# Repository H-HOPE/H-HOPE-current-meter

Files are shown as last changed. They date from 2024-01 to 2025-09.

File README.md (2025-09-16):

<div align="right">
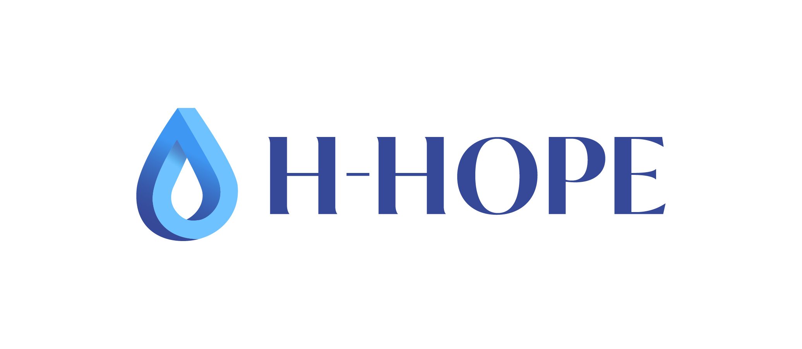
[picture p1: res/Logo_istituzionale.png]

</div>

# DIY water current meter for measuring flow velocities 'H-HOPE water current meter'

The water current meter "H-HOPE water current meter" was designed and developed as part of a H-HOPE project (web site https://h-hope.eu/). H-HOPE water current meter measures water flow velocities on the principle of automatic recalculation of screw rotation frequencies in water velocity through the equation. H-HOPE water current meter has been designed to be produced using the DIY (Do-It-Yourself) principle. All parts used for the production of H-HOPE water current meter are readily available. H-HOPE water current meter can be powered by 9V battery, or by external micro USB cable. H-HOPE water current meter can measure water velocity from 0.1 to 5m/s. 

<div align="center">
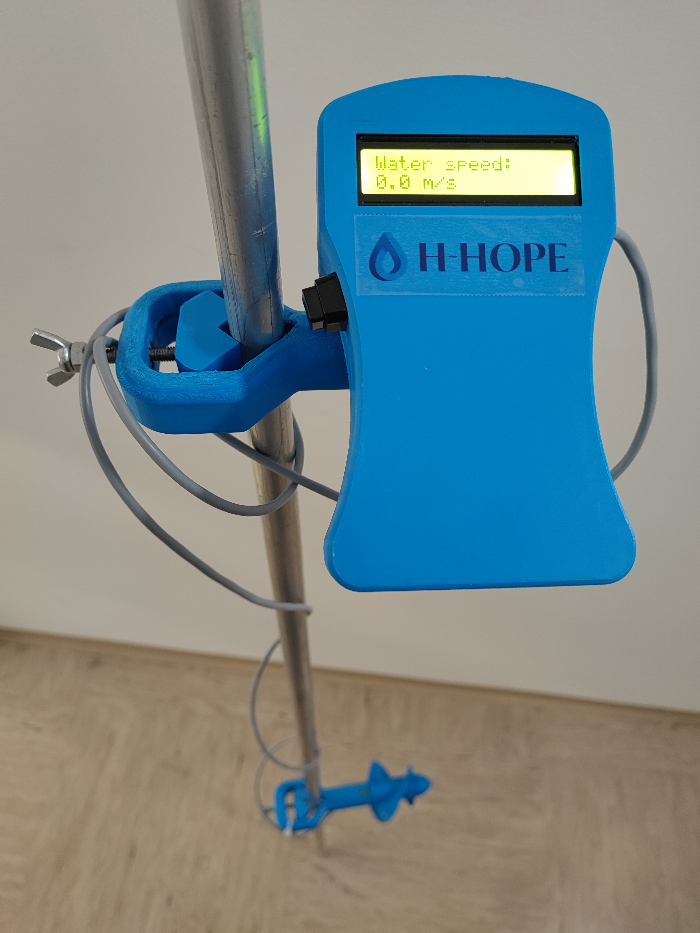
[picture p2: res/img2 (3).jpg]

 
Figure. H-HOPE water current meter.</div>

<div align="center">
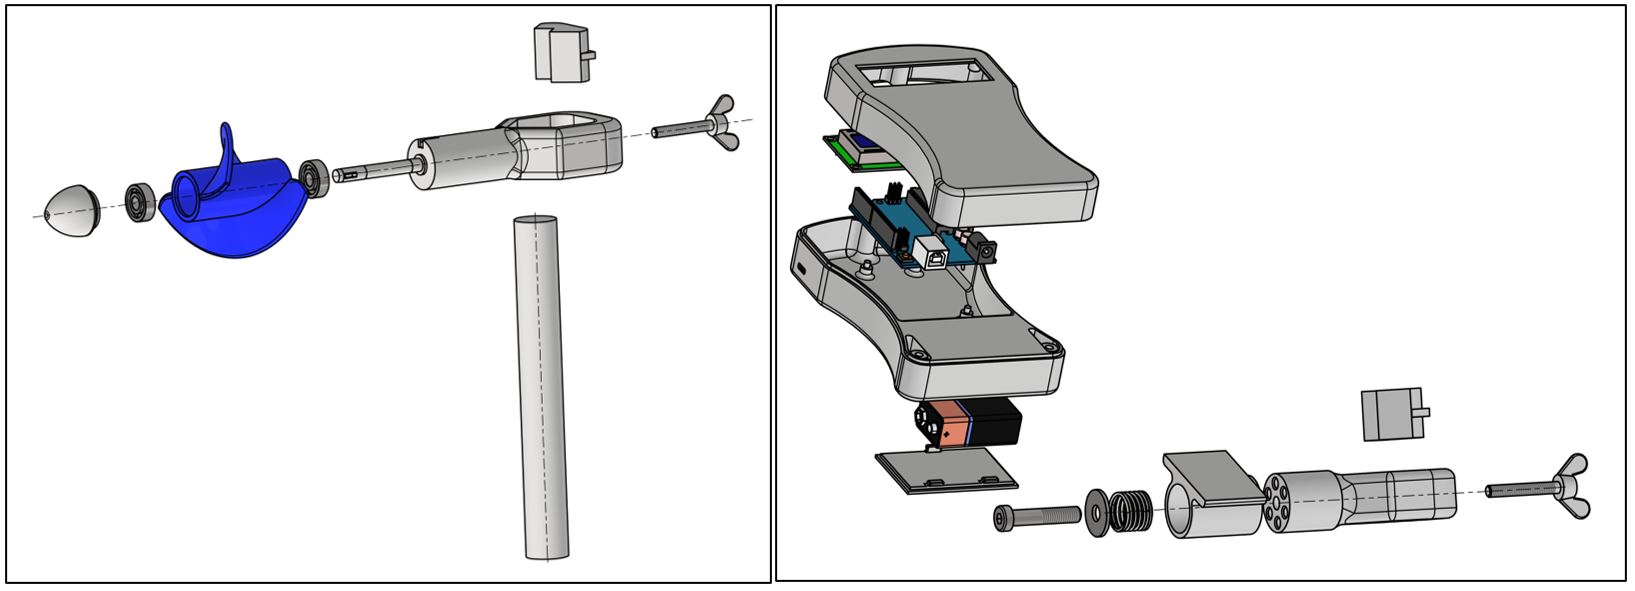
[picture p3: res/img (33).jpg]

 
Figure. 3D exploded model of a H-HOPE water current meter.</div>

## Table of content

- [Materials and tools,](#material)
- [3D model,](#3dmodel)
- [Arduino code,](#arduino)
- [Assembly and test,](#assembly)
- [Field test.](#fieldtest)

## Material and tools used

The project was designed in a certain way, that the material and tools necessary to build this project is widely available. Most of the parts and tools are available in local technical store or for example on online store Aliexpress. 

### Material used for this project:

- Arduino uno https://www.aliexpress.com/item/1005002707450245.html
- Connectors (XH): https://www.aliexpress.com/item/33000442968.html
- Connecting cables (XH): https://www.aliexpress.com/item/1005002160765607.html
- Micro usb socket: https://www.aliexpress.com/item/1005003730290423.html
- 9v battery holder https://www.aliexpress.com/item/32825539506.html
- 16x2 LCD with i2c header: https://www.aliexpress.com/item/32413056677.html
- Unipolar Hall sensor (SIP package, for exmaple SS443A): https://www.aliexpress.com/item/1005001522952951.html
- Magnet, size 3x1mm: https://www.aliexpress.com/item/1005005222147418.html
- 2m 3-core cable: https://www.aliexpress.com/item/1005002082473369.html
- Pushbutton / toggle ON/OFF switch: https://www.aliexpress.com/item/1005004004236347.html
- XH pin connectors: https://www.aliexpress.com/item/1005004267331222.html
- 6x M2 screws (10mm length)
- 3x M4 screws (30mm length)
- 2x M5 screws with 
- M8 screw (50mm length)
- Epoxy glue
- 9v battery
- micro usb cable
- spring
- Stick, Bar

### Tools needed for this project:

- Soldering iron
- 3D printer
- Set of Screwdrivers

## 3D printing and model of the H-HOPE water current meter

We used Prusa MK3S 3D printer to print the H-HOPE water current meter plastic parts. Chosen material was PETG.

Below is the 3D exploded model of a H-HOPE water current meter. H-HOPE water current meter is made from two main parts. 

- assembly of a screw,
- assembly of the enclosure with LCD screen and holder. 

<div align="center">
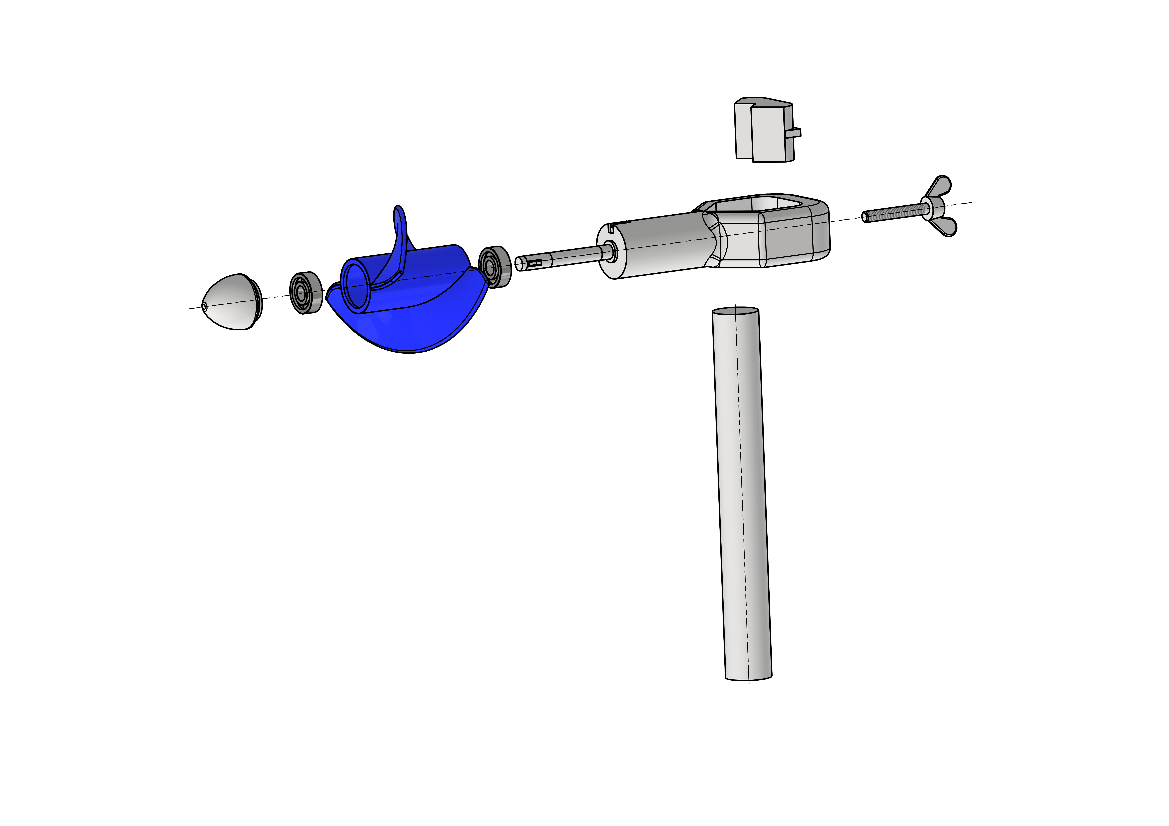
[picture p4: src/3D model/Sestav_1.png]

 
Figure. Exploded model of the screw.</div>

<div align="center">
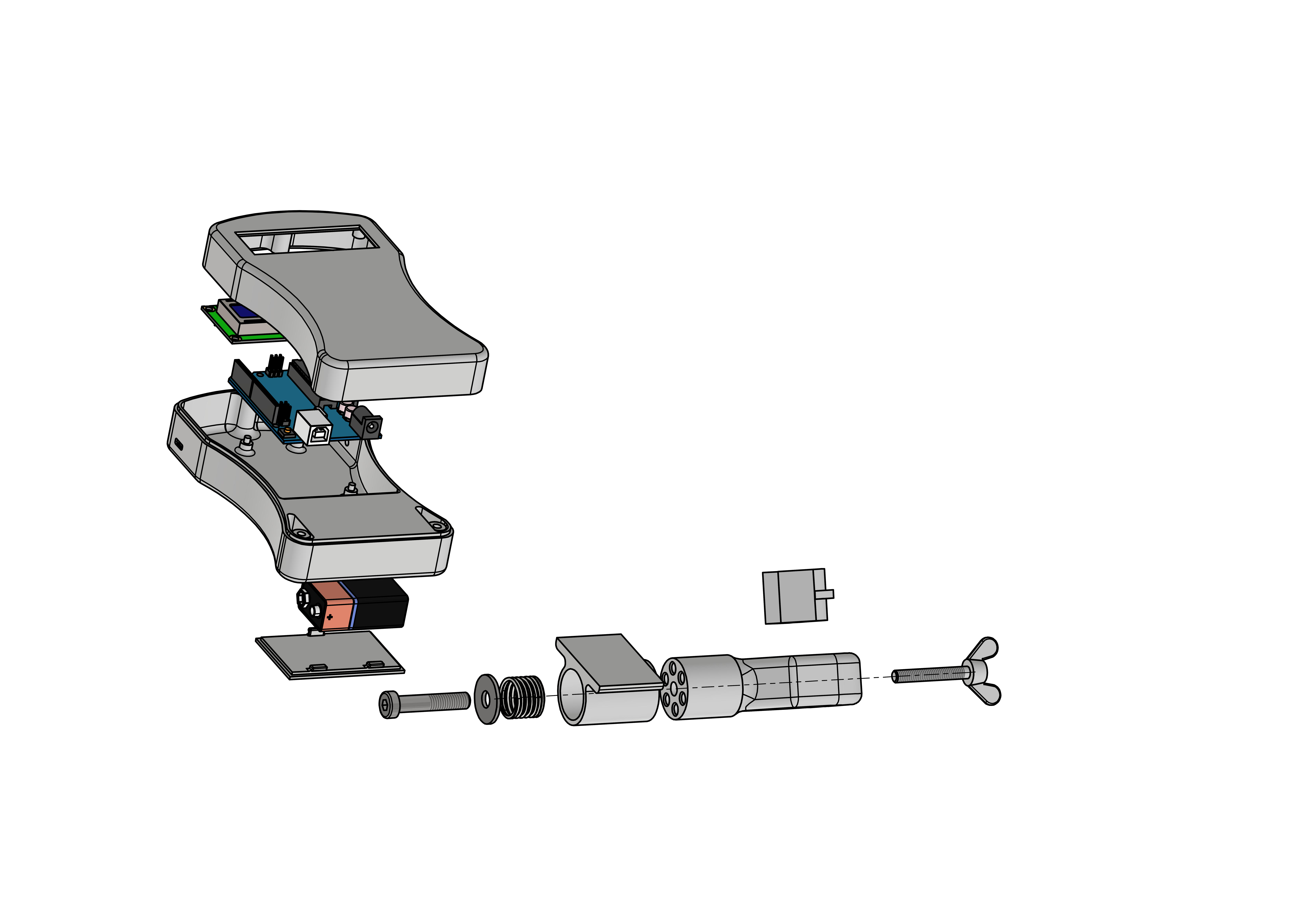
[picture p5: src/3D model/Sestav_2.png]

 
Figure. Exploded model of the enclosure with LCD screen and holder.</div>

Source files (in STEP and STL format) for printing the H-HOPE water current meter are available on Github: [STEP files](https://github.com/H-HOPE/H-HOPE-current-meter/tree/main/src/3D%20model/STEPfiles), [STL files](https://github.com/H-HOPE/H-HOPE-current-meter/tree/main/src/3D%20model/STLfiles).

<div align="center">
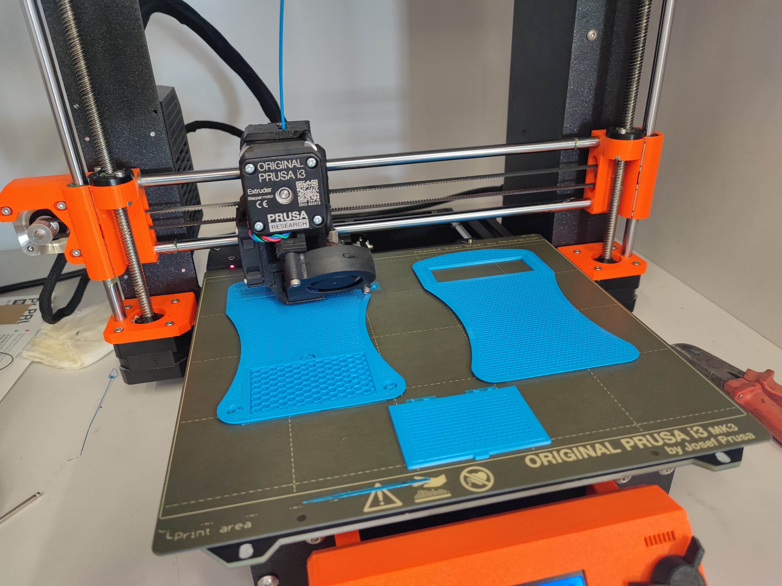
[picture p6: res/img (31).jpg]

 
Figure. Printing the H-HOPE water current meter enclosure.</div>

<div align="center">
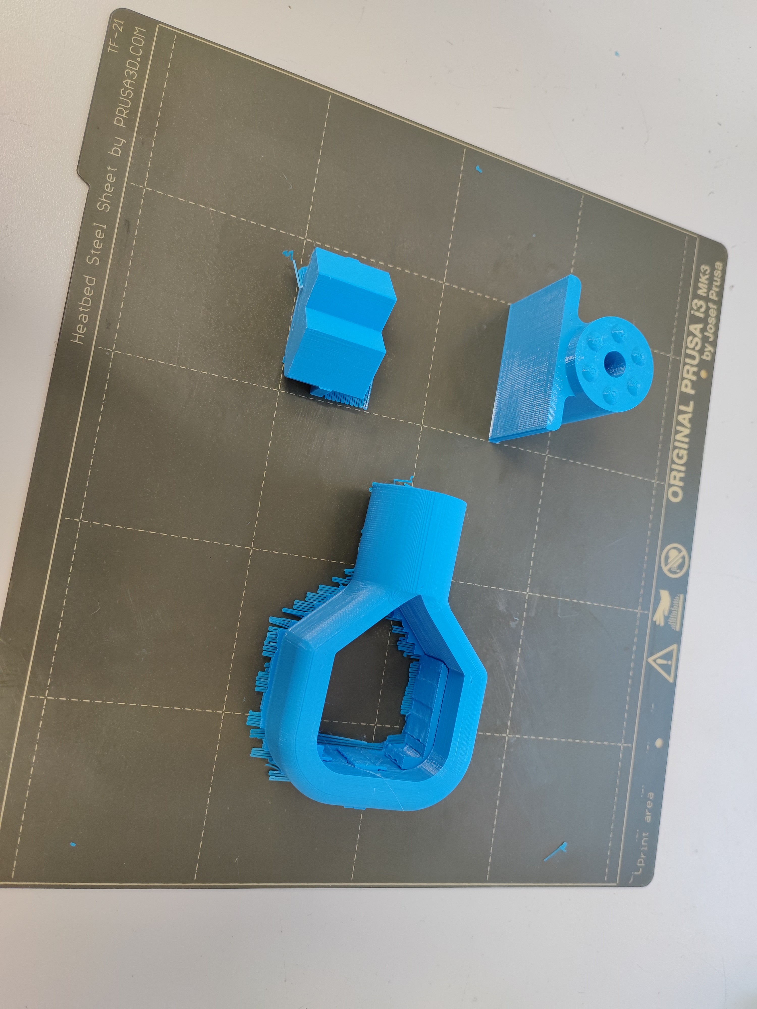
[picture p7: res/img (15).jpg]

 
Figure. 3D printed parts for the H-HOPE water current meter holder.</div>

## Arduino code

In this chapter the source code for the Arduino Uno microcontroller will be explained.

<div align="center">
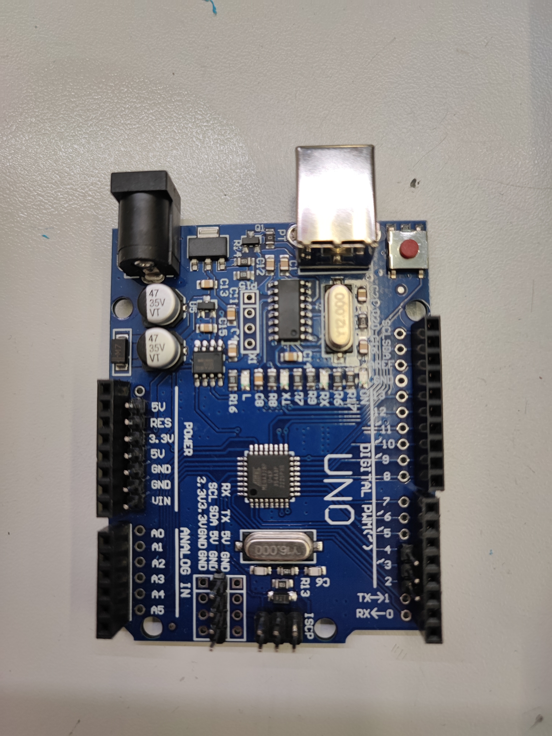
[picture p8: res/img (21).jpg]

 
Figure. Arduino uno board is used for H-HOPE water current meter electronics.</div>

Arduino code:
https://github.com/H-HOPE/DIY_Flow_meter/blob/e5a896e44799b07652782b1dd13d3e7614e1950c/src/Arduino/H-HOPE_Hi-wing.ino#L1-L63

Key parts of the Arduino code:
- First, we include libraries for LCD screen and I2C protocol. LCD screen library is also available [here](https://github.com/H-HOPE/DIY-Flow-meter/tree/main/src/Arduino/lib).
- Then we define an Arduino pin, where the hall sensor will be connected. In this case, this pin is number 2.
- in lines 13 through 15 we define variables. 
- In the setup section we initialize the LCD screen and configure interrupt for the hall sensor. 
Hall sensor output is connected to the Arduino Uno inetrrupt. Arduino Uno has two external interrupt pins, INT0 and INT1, which are mapped to digital pins 2 and 3 respectively. Interrupts are signals that allow a microcontroller to pause its current execution and handle an event or task that has a higher priority. 
In this case hall sensor is attached to the INT0 pin (digital pin 2).
Configure the interrupt settings using the attachInterrupt() function. This function takes three arguments: the interrupt number (in this case, 0 for INT0), the function to call when the interrupt is triggered (cnt), and the mode in which to trigger the interrupt (on FALLING EDGE).
- In the loop section, from line 38, the code to calculate the water velocity from the screw rotation speed is written. The calculated water velocity is shown on the LCD screen.
- Finally at the end of the program there is an interrupt routine, that records the time when the magnet on the wing passes hall sensor.

<div align="center">
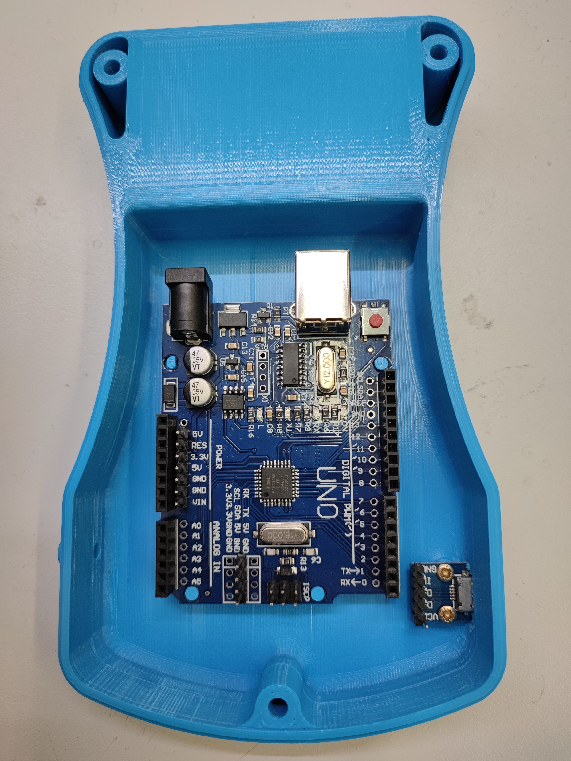
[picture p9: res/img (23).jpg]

 
Figure. Arduino Uno microcontroller mounted in the H-HOPE water current meter enclosure.</div>

## Assembly and test

With all the printed parts ready and programmed Arduino, we can start the assembly of the H-HOPE water current meter.

3D exploded model of a H-HOPE water current meter

<div align="center">

 
Figure. 3D exploded model of a screw.</div>

<div align="center">

 
Figure. 3D exploded model of the enclosure.</div>

### Enclosure for the H-HOPE water current meter electronics

<div align="center">
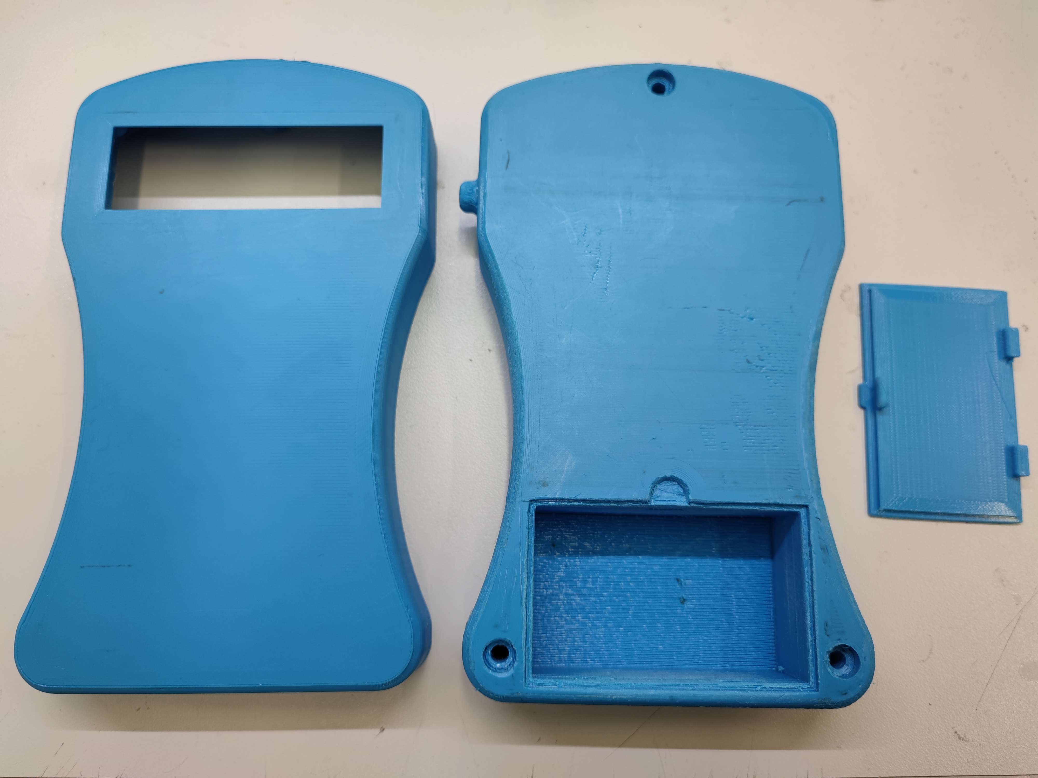
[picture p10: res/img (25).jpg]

 
Figure. Enclosure for the H-HOPE water current meter electronics.</div>

Assembly of the screw:

Mount two bearings in the screw and put the end cap to the screw.

<div align="center">
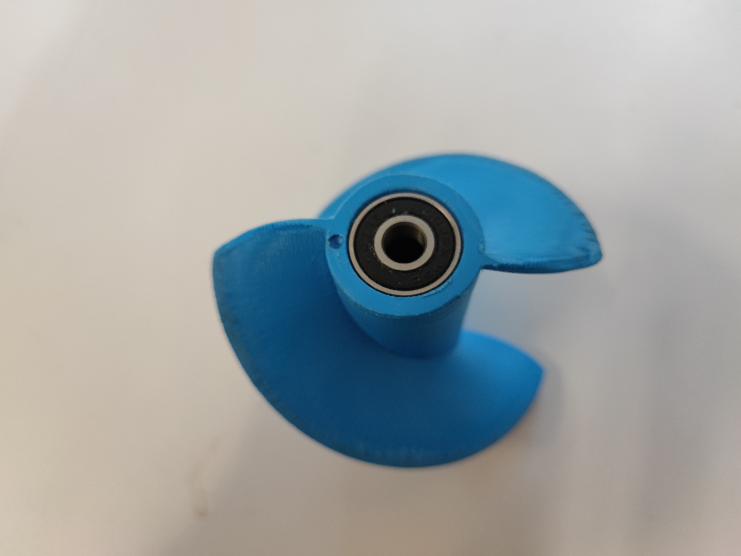
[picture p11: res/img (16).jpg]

 
Figure. First bearing mount.</div>

<div align="center">
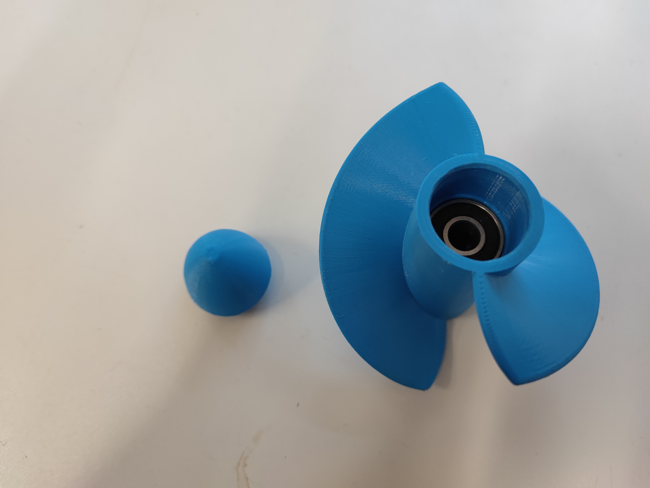
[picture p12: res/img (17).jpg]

 
Figure. Second bearing mount, with end cap.</div>

<div align="center">
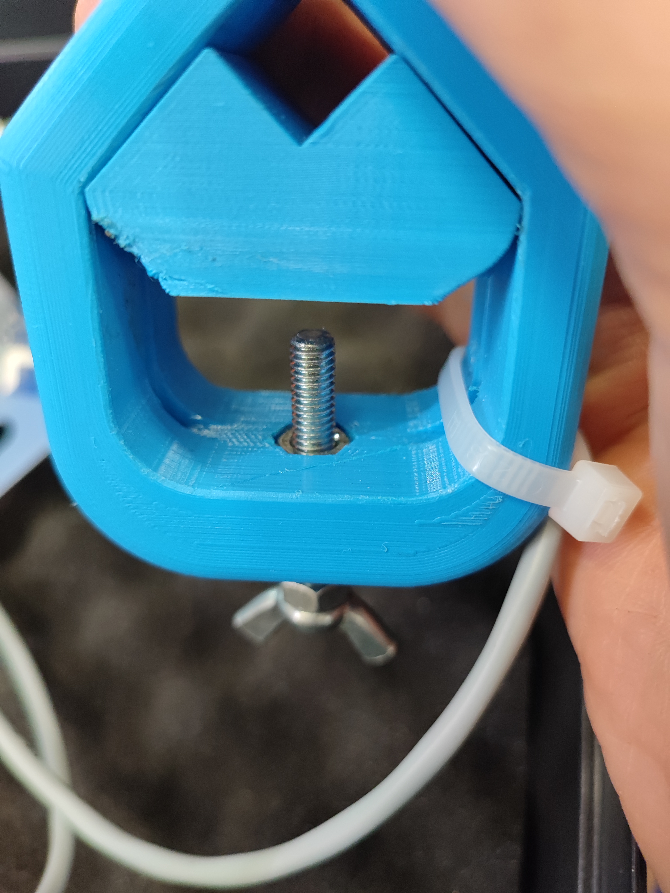
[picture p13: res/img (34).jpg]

 
Figure. Assembly of the bar mounting tight screw</div>

<div align="center">
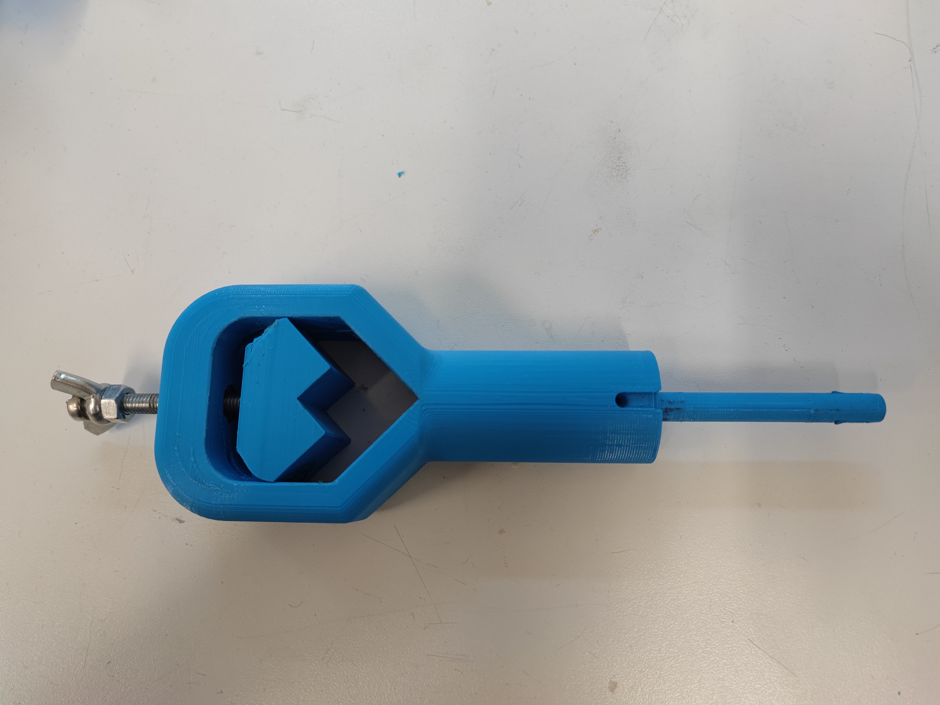
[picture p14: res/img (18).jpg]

 
Figure. Assembled screw holder.</div>

Next, place 1x3 mm magnet in the prefabricated hole in the screw and glue the magnet with Epoxy glue.
<div align="center">
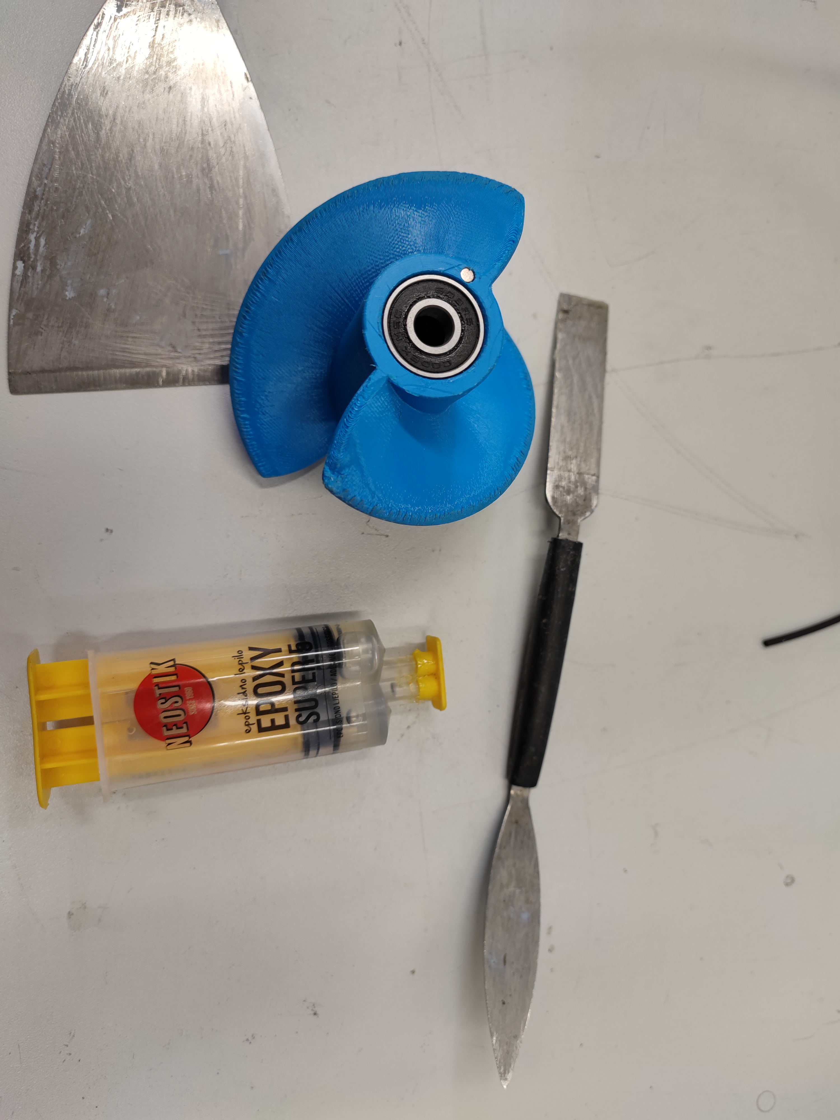
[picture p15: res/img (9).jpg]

 
Figure. Magnet assembly on the screw.</div>

We need to solder hall sensor to the cable. Hall sensor has three pins GND, VCC and Signal

<div align="center">
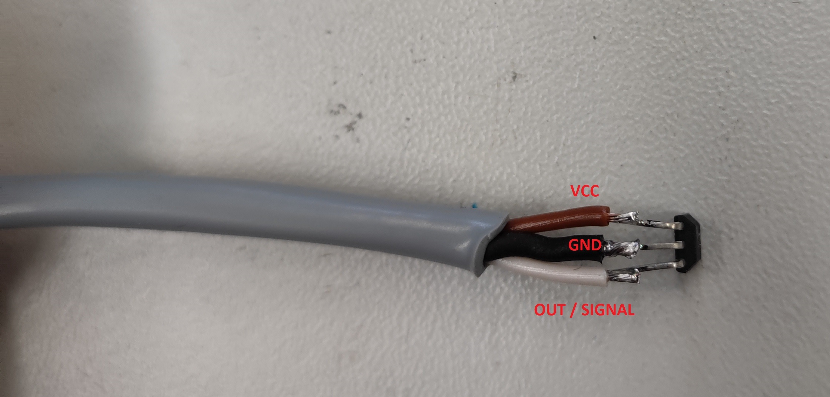
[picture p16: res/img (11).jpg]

 
Figure. Pinout of the SS443a Hall sensor.</div>

Put the cable through the screw holder and glue the hall sensor, with the Epoxy glue to the screw holder.

<div align="center">
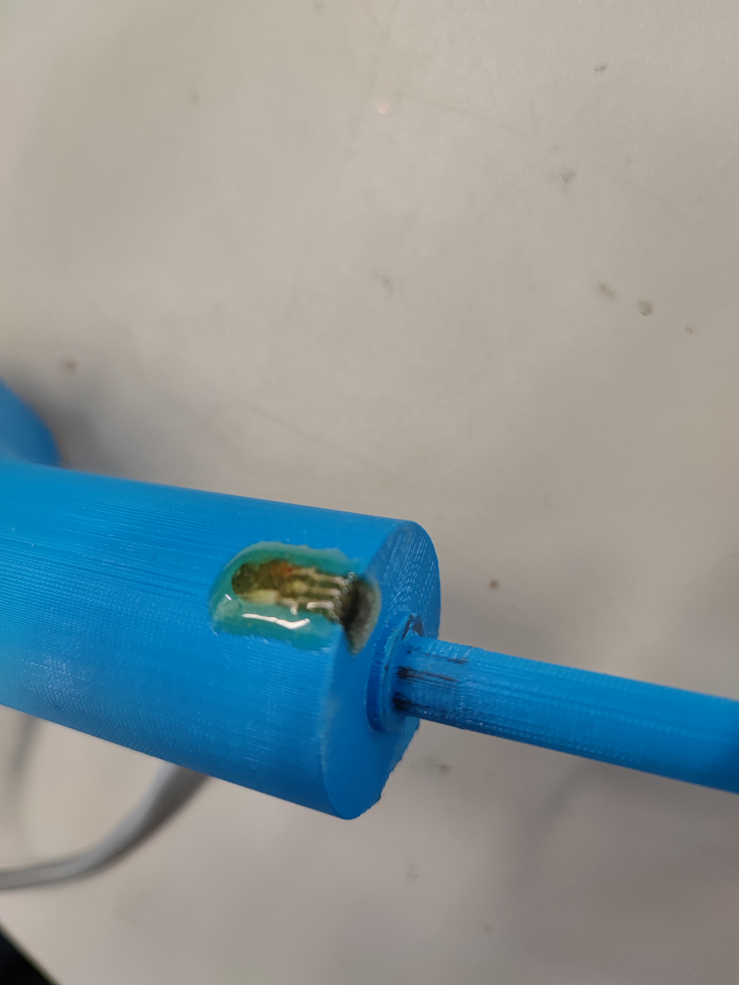
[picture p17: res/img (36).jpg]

 
Figure. Screw with bearing and end cap.</div>

Assembled Screw.
<div align="center">
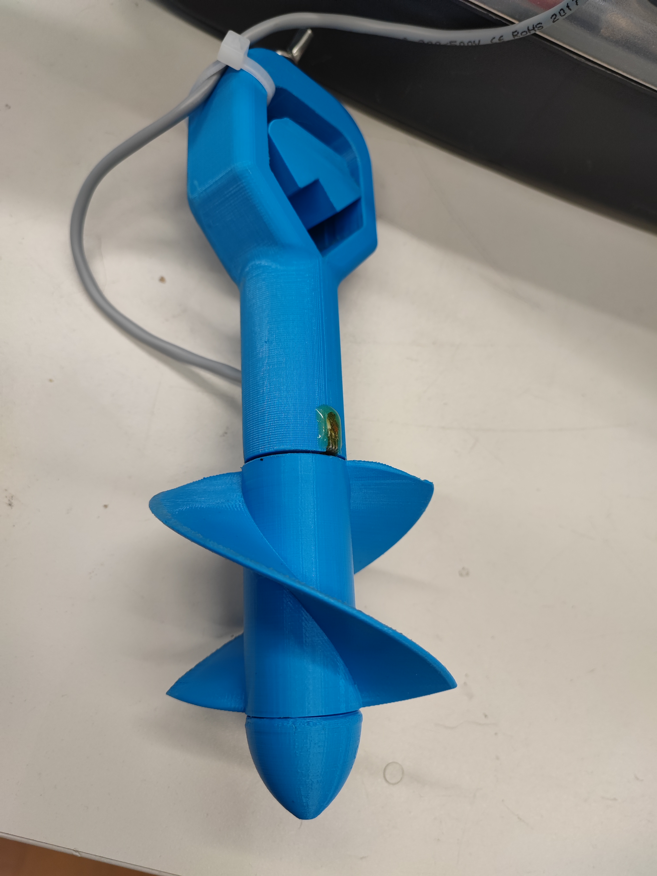
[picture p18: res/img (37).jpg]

 
Figure. Assembled Screw.</div>

### Assembly of the H-HOPE water current meter electronics.

Mount the Arduino Uno in the enclosure, screw the micro USB module to the enclosure with two M2 10mm screws. Connect micro USB module to Arduino Uno (5V to 5V; GND to GND).
<div align="center">

 
Figure. Arduino Uno and micro USB module.</div>

Connect hall sensor GND, VCC and OUT to the Arduino Uno
<div align="center">
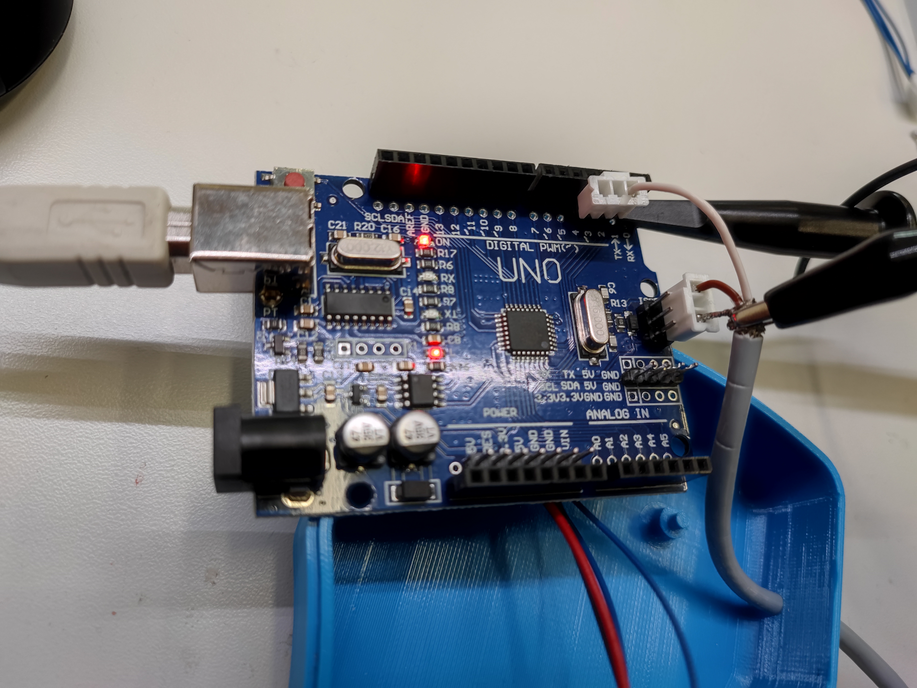
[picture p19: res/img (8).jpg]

 
Figure. Hall sensor connected to the Arduino Uno.</div>

Mount 16x2 LCD screen with 4 M2 10mm screws to the front of the enclosure. Connect the LCD screen to the Arduino, through the I2C protocol.
<div align="center">
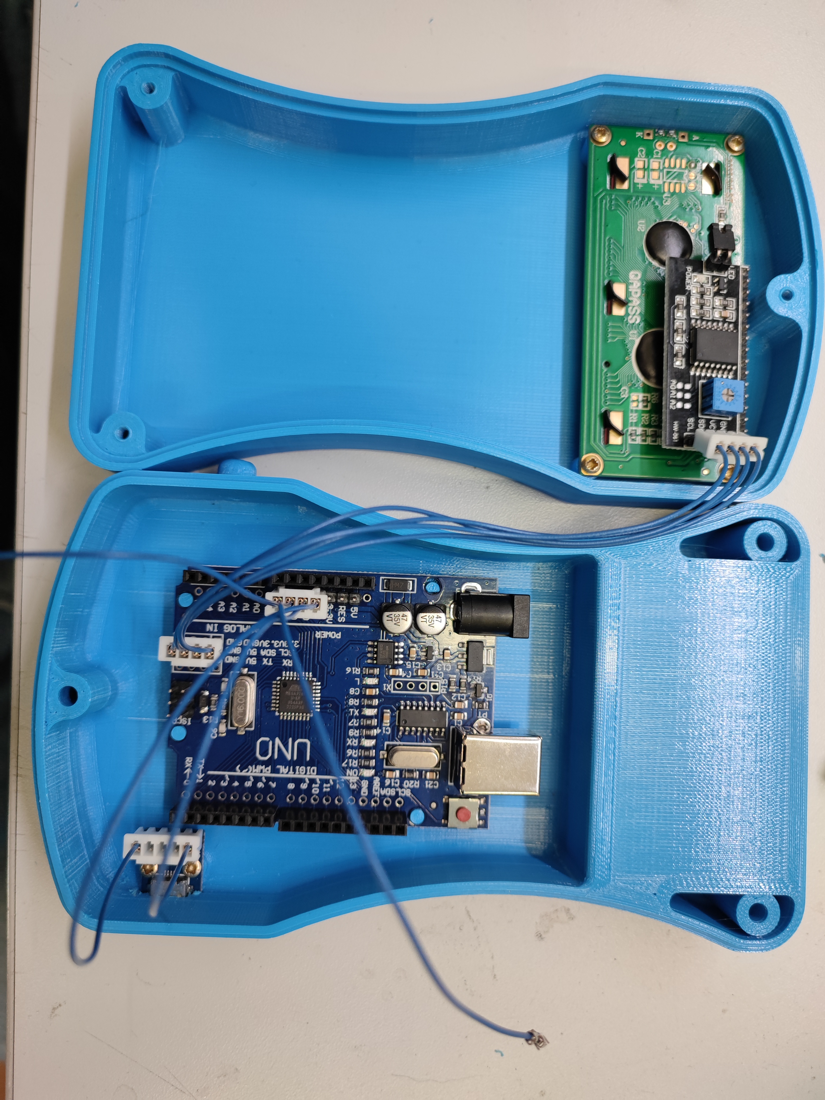
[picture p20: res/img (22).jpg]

 
Figure. LCD screen connection.</div>

Mount 9V battery connector, make small hole for wires. Connect 9v Battery holder to Arduino Uno (+9V battery to Vin Arduino Uno pin; -9V battery to GND Arduino Uno pin)
<div align="center">
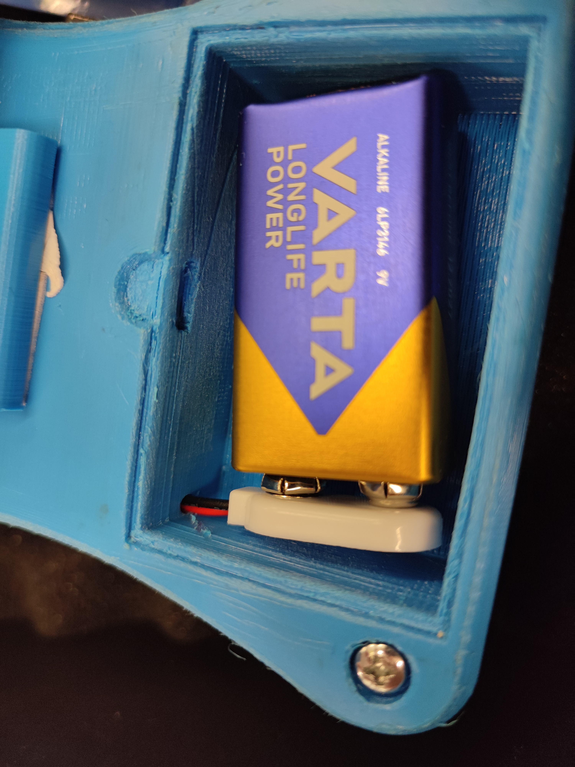
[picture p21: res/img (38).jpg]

 
Figure. 9V battery installation.</div>

Make hole on the enclosure for the external ON/OFF switch to power on the H-HOPE water current meter. Connect the switch in series with positive battery wire.
<div align="center">
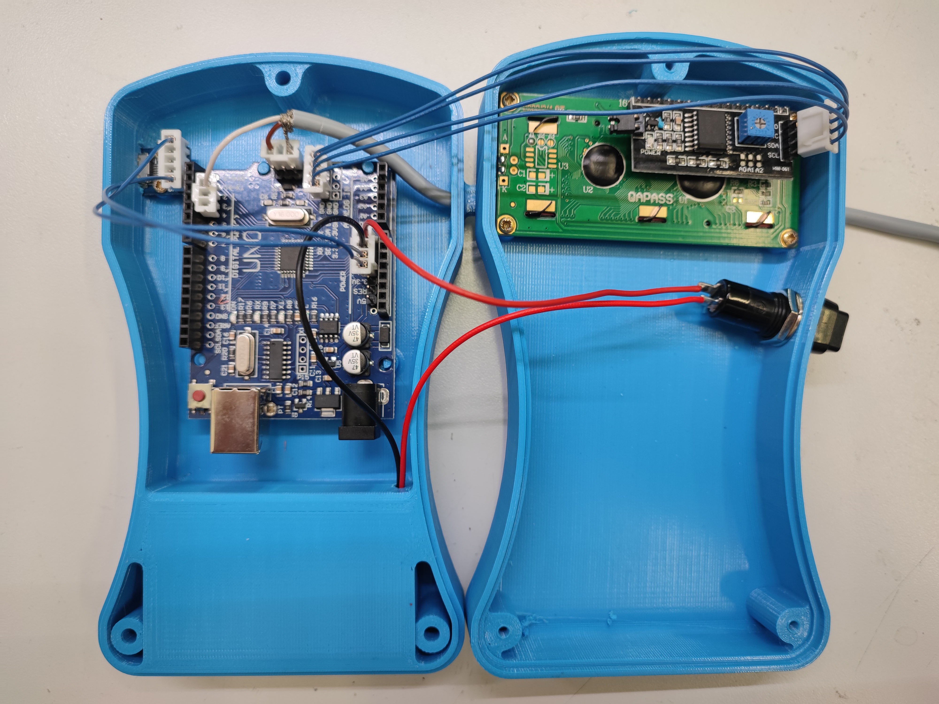
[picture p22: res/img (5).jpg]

 
Figure. External ON/OFF switch.</div>

Use screws to assemble the electronics enclosure of the H-HOPE water current meter. 
<div align="center">
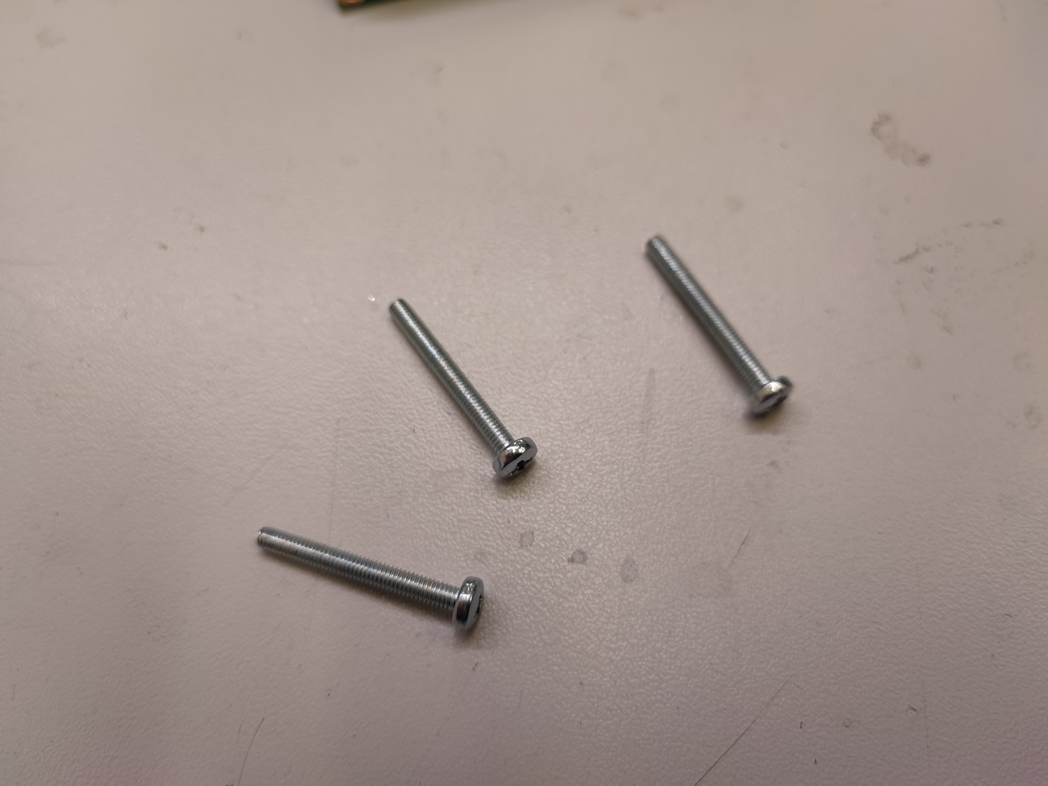
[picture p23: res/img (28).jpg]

 
Figure. Mounting screws.</div>

### Holder for the H-HOPE water current meter electronics (optional)

It is also possible to mount the H-HOPE water current meter electronics with the help of holder to the stick. In that case you need to print and assemble the H-HOPE water current meter holder. 

<div align="center">
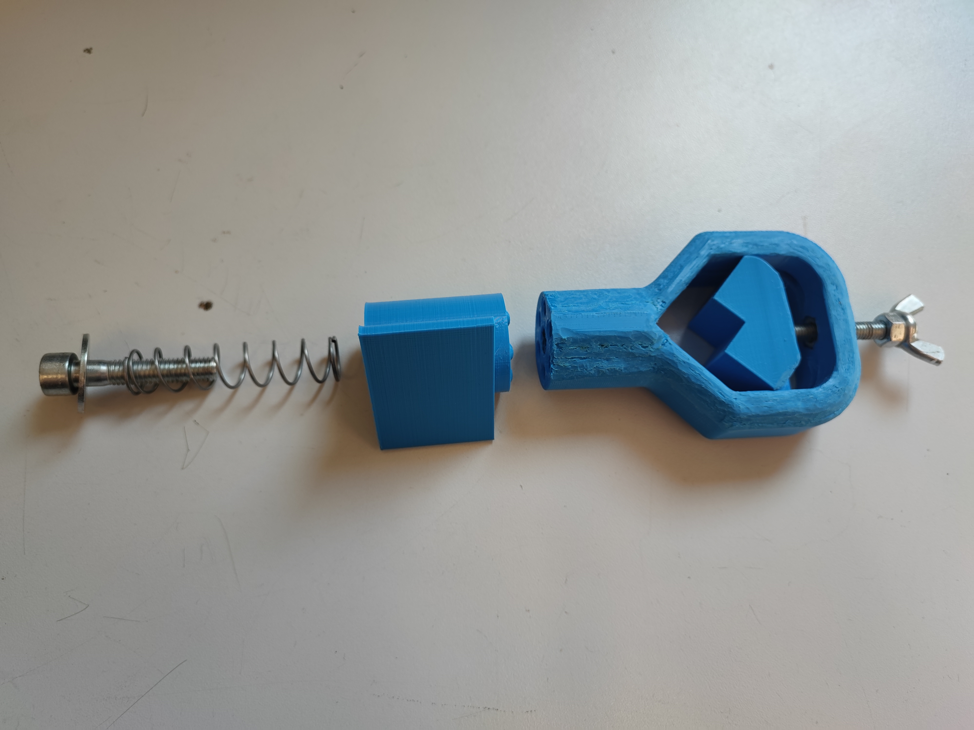
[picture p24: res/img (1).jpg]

 
Figure. Assembly of the holder for the H-HOPE water current meter electronics.</div>

### Test hall sensor response.

Oscilloscope was used to test the output signal from the hall sensor

<div align="center">
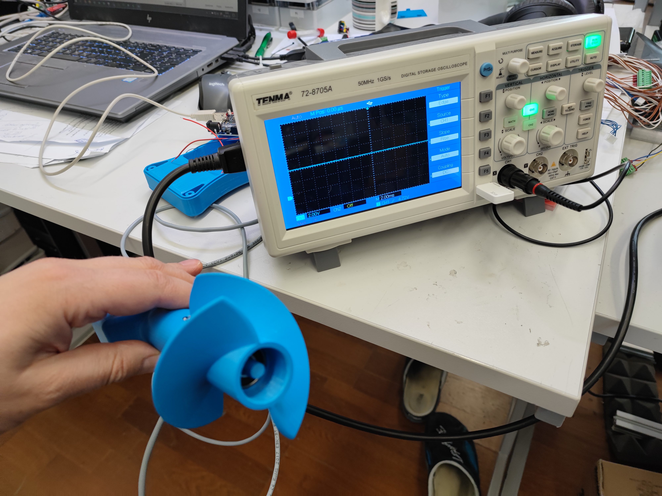
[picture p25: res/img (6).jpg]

 
Figure. Hall sensor test setup.</div>

Hall sensor need pull-up resistor to operate properly. You can use external 10k pull-up resistor across the Vcc and hall input pin. In our case we configured Arduino to use his internal pull-up resistor. Then we test the operation of the hall sensor with an oscilloscope.

<div align="center">
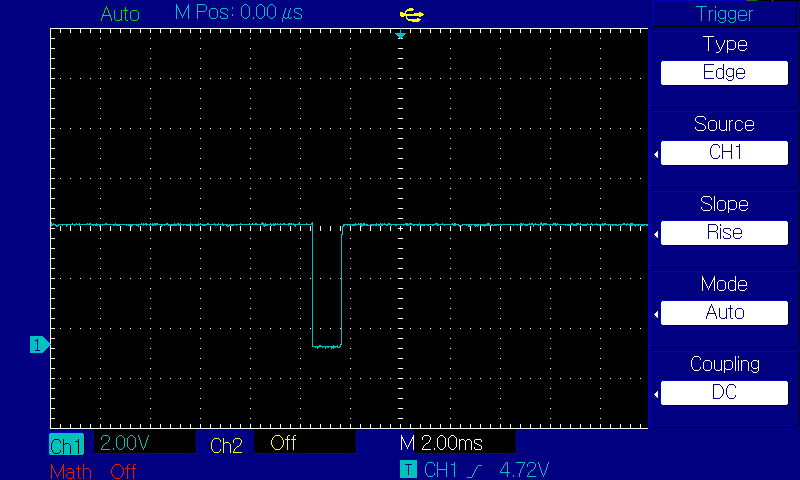
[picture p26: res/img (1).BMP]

 
Figure. Hall sensor output signal on oscilloscope.</div>

## Field test

Now you can find a waterway and measure its speed with the H-HOPE water current meter, water velocity sensor.

<div align="center">
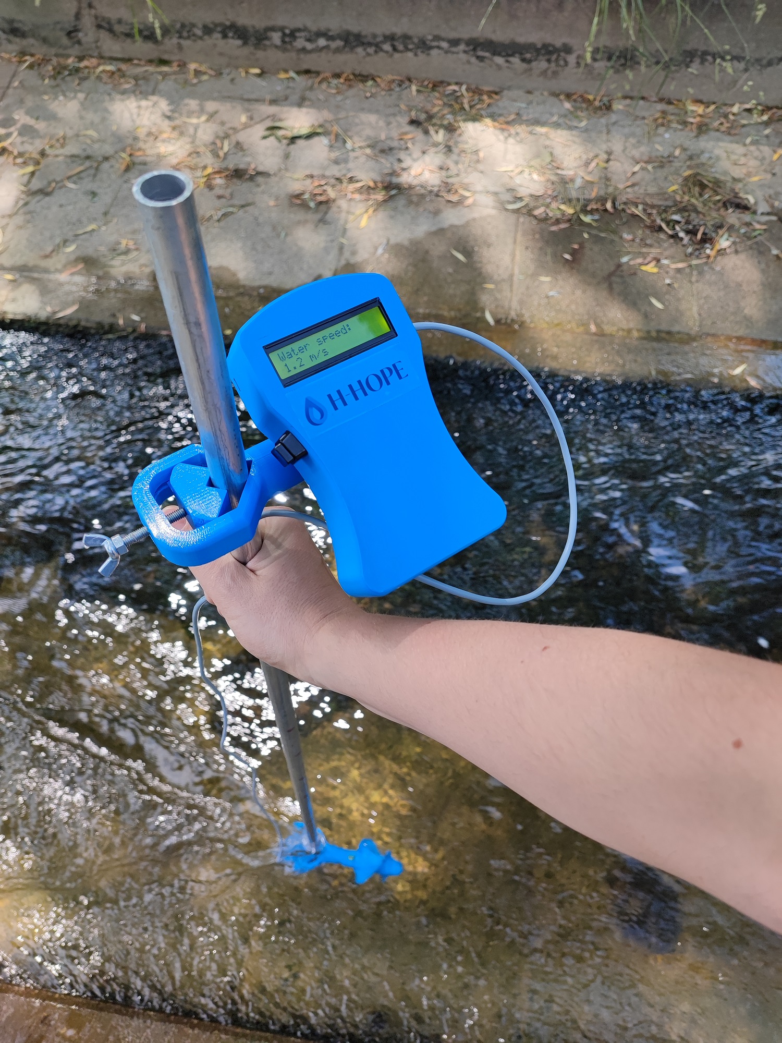
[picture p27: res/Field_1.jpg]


Figure. Image of the H-HOPE water current meter water velocity sensor in open channel
 
 <div align="center">
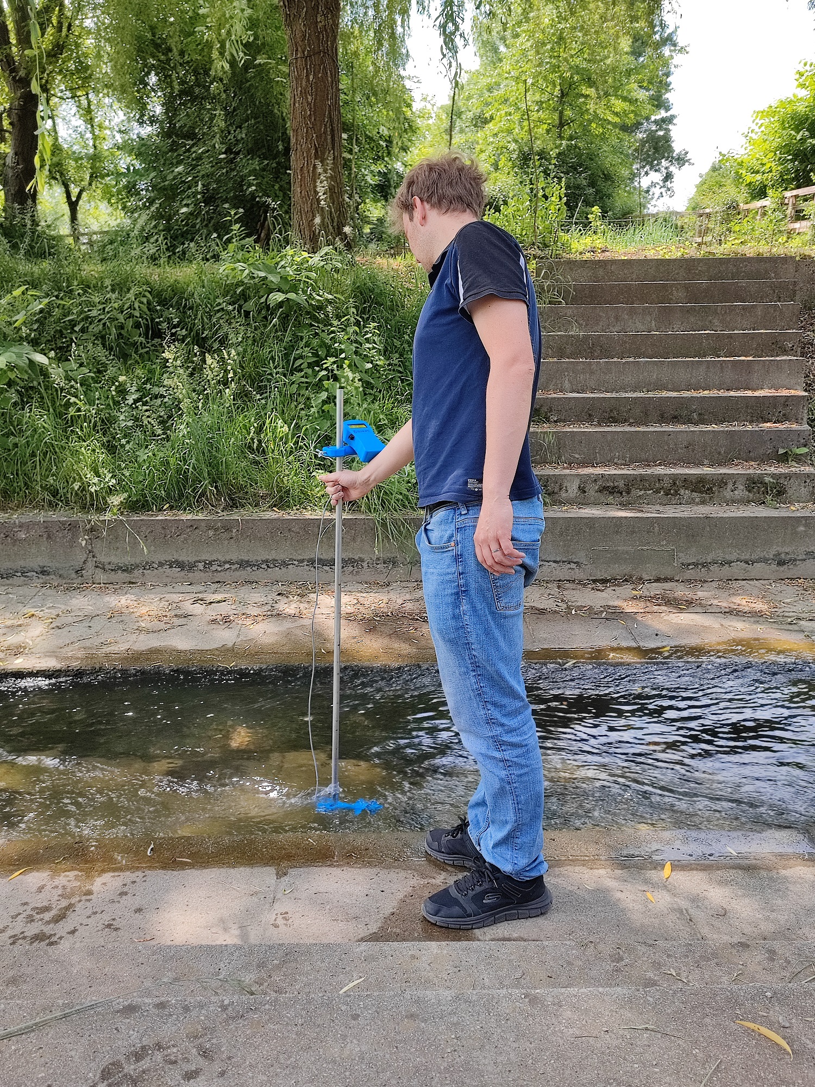
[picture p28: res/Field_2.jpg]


Figure. Measuring water velocity with the H-HOPE water current meter sensor.

&nbsp;
&nbsp;
&nbsp;

<div align="center">
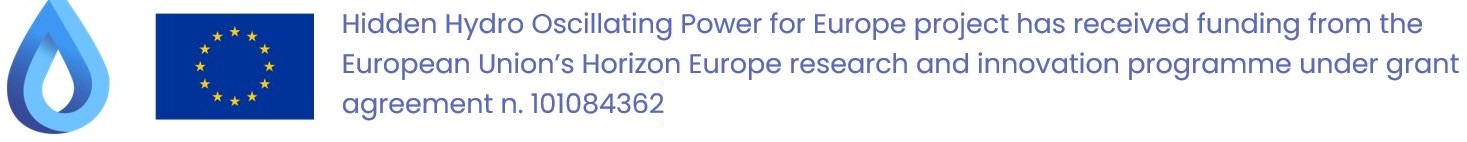
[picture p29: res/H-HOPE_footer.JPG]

</div>

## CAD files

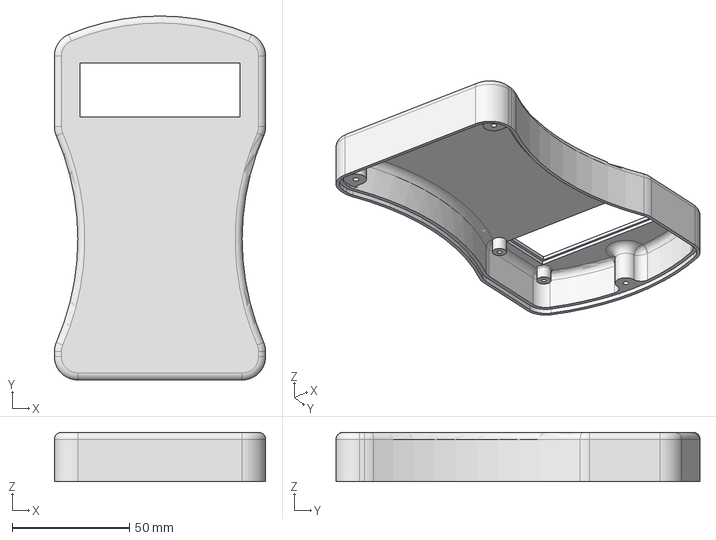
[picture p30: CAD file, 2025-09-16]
src/3D model/STEPfiles/Box Cover.stp
90.0 x 155.0 x 21.0 mm

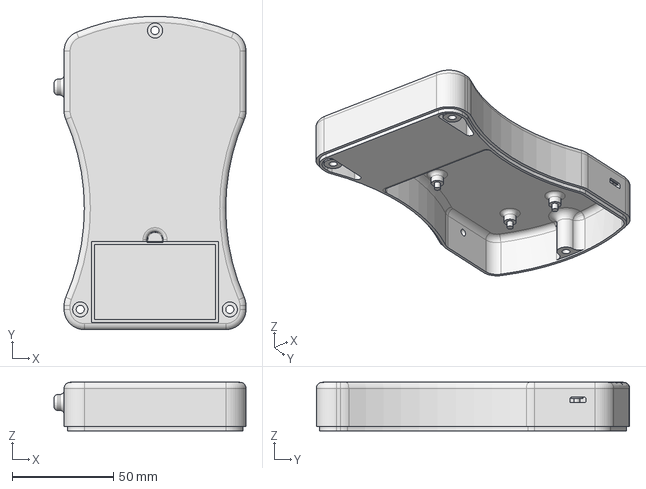
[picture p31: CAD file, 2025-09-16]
src/3D model/STEPfiles/Box Bottom.stp
95.0 x 155.0 x 24.0 mm

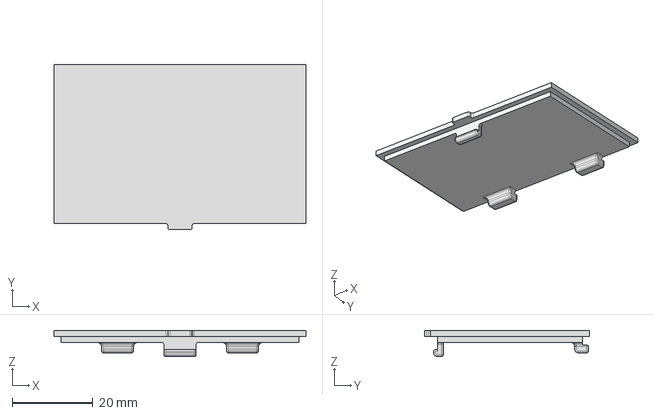
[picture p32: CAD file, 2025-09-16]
src/3D model/STEPfiles/Battery Cover.stp
62.5 x 41.0 x 6.50 mm

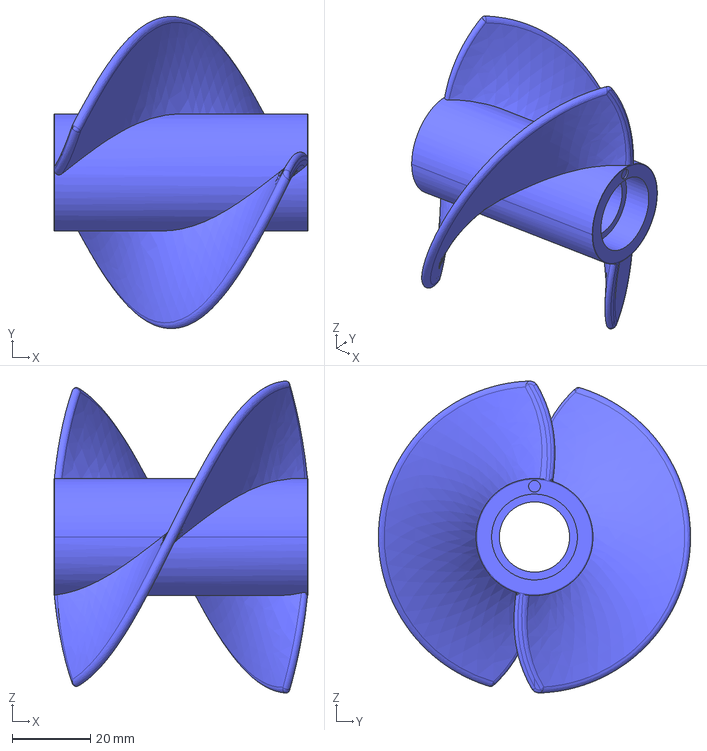
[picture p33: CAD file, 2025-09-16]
src/3D model/STEPfiles/Rotor.stp
65.0 x 80.0 x 80.0 mm

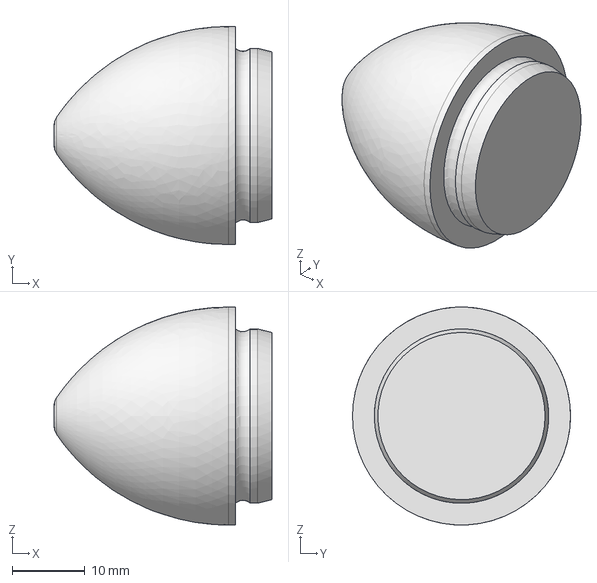
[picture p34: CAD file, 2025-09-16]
src/3D model/STEPfiles/Cap.stp
30.0 x 30.0 x 30.0 mm

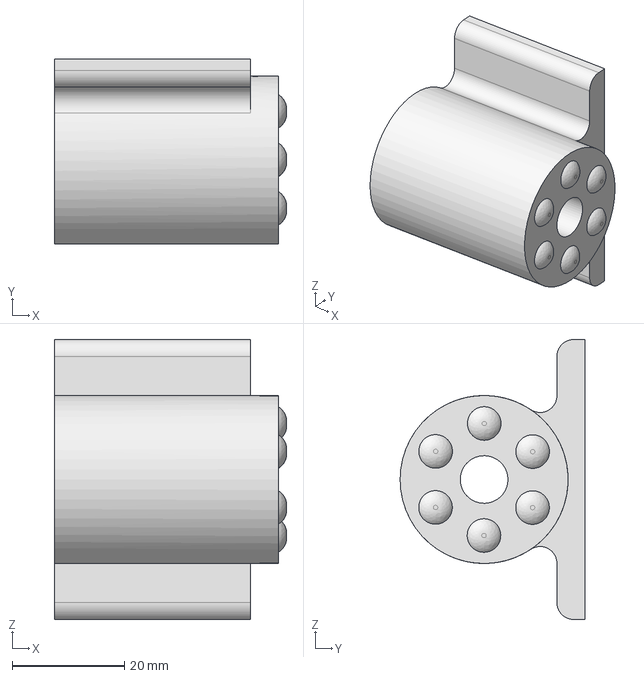
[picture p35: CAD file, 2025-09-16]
src/3D model/STEPfiles/Movable Part of Holder.stp
41.5 x 33.0 x 50.0 mm

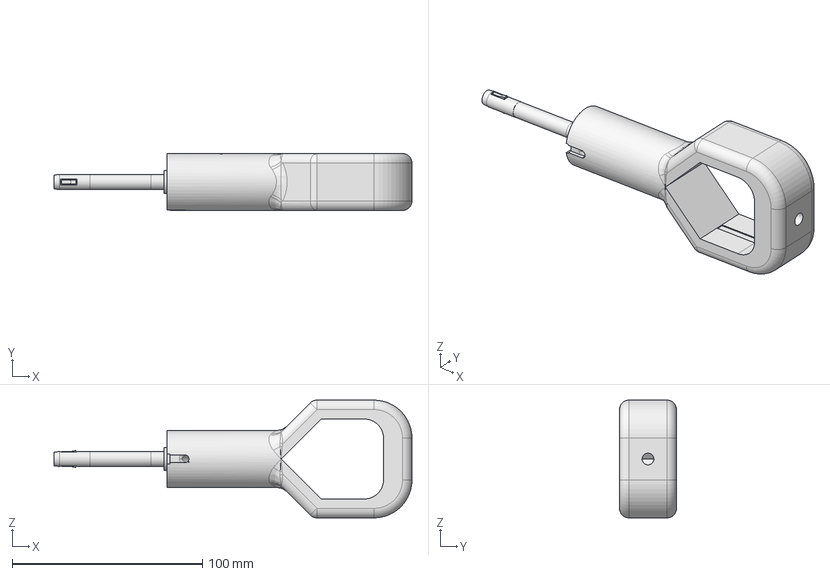
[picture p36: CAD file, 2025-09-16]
src/3D model/STEPfiles/Holder.stp
188.4 x 30.0 x 62.0 mm

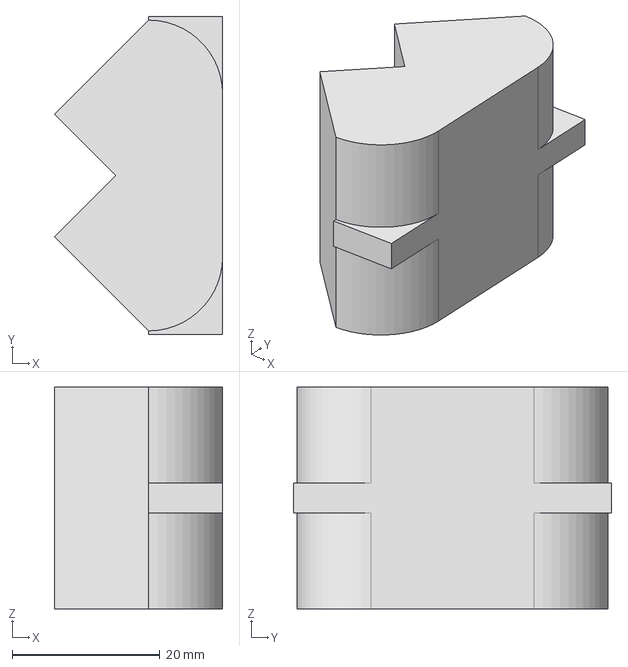
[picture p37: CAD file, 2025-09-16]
src/3D model/STEPfiles/Slider.stp
22.7 x 43.0 x 30.0 mm

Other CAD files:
src/3D model/STLfiles/Battery Cover.stl
src/3D model/STLfiles/Box Bottom.stl
src/3D model/STLfiles/Box Cover.stl
src/3D model/STLfiles/Cap.stl
src/3D model/STLfiles/Holder.stl
src/3D model/STLfiles/Movable Part of Holder.stl
src/3D model/STLfiles/Rotor.stl
src/3D model/STLfiles/Slider.stl
src/3D model/hi_wing_Inventor.iam

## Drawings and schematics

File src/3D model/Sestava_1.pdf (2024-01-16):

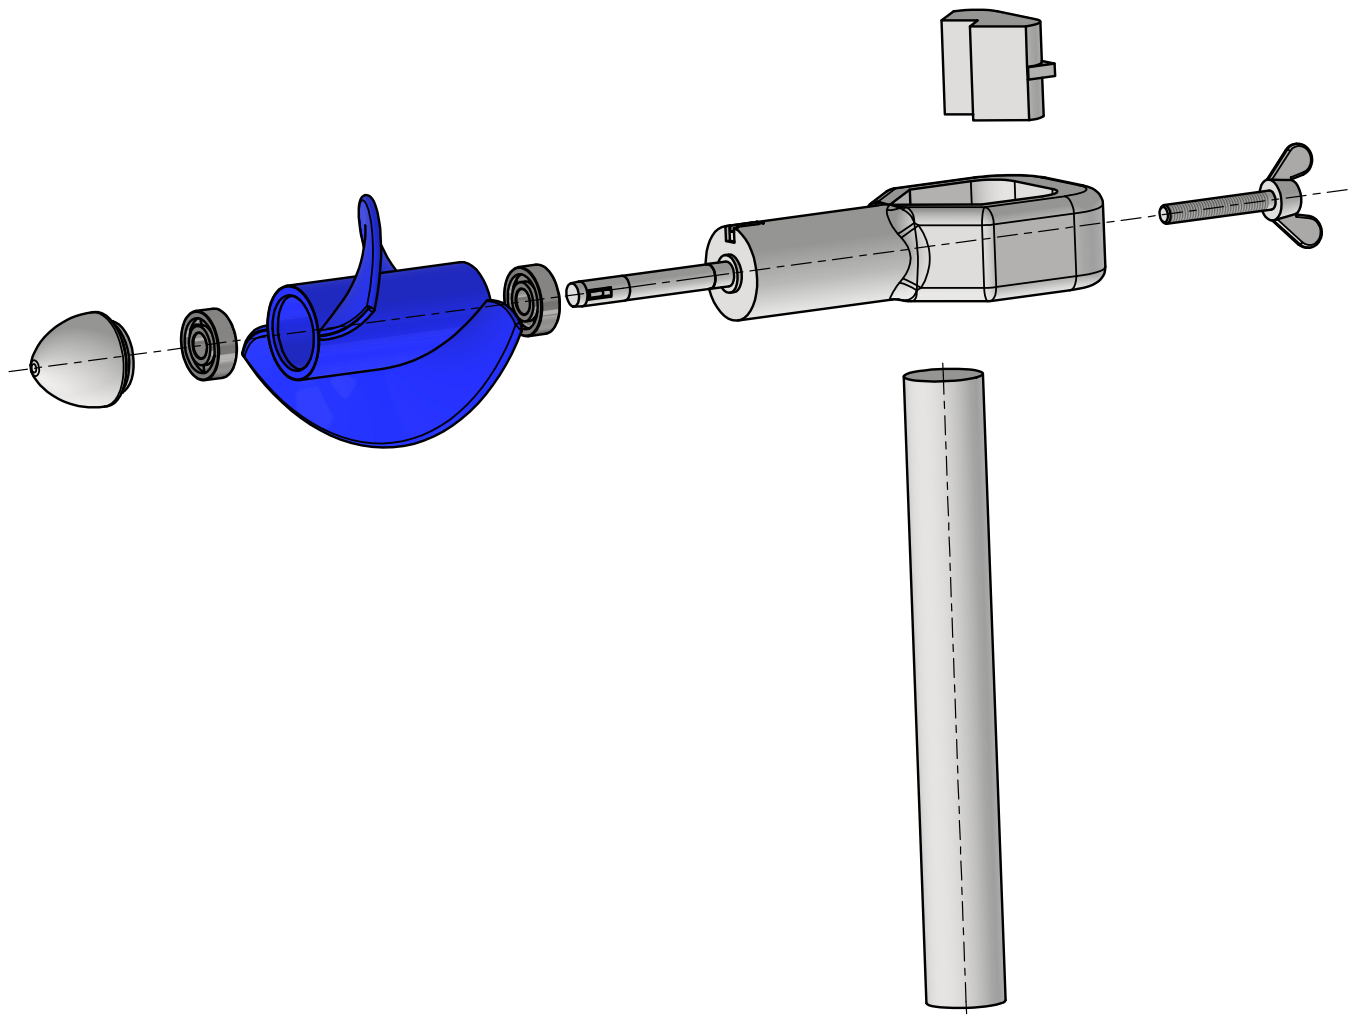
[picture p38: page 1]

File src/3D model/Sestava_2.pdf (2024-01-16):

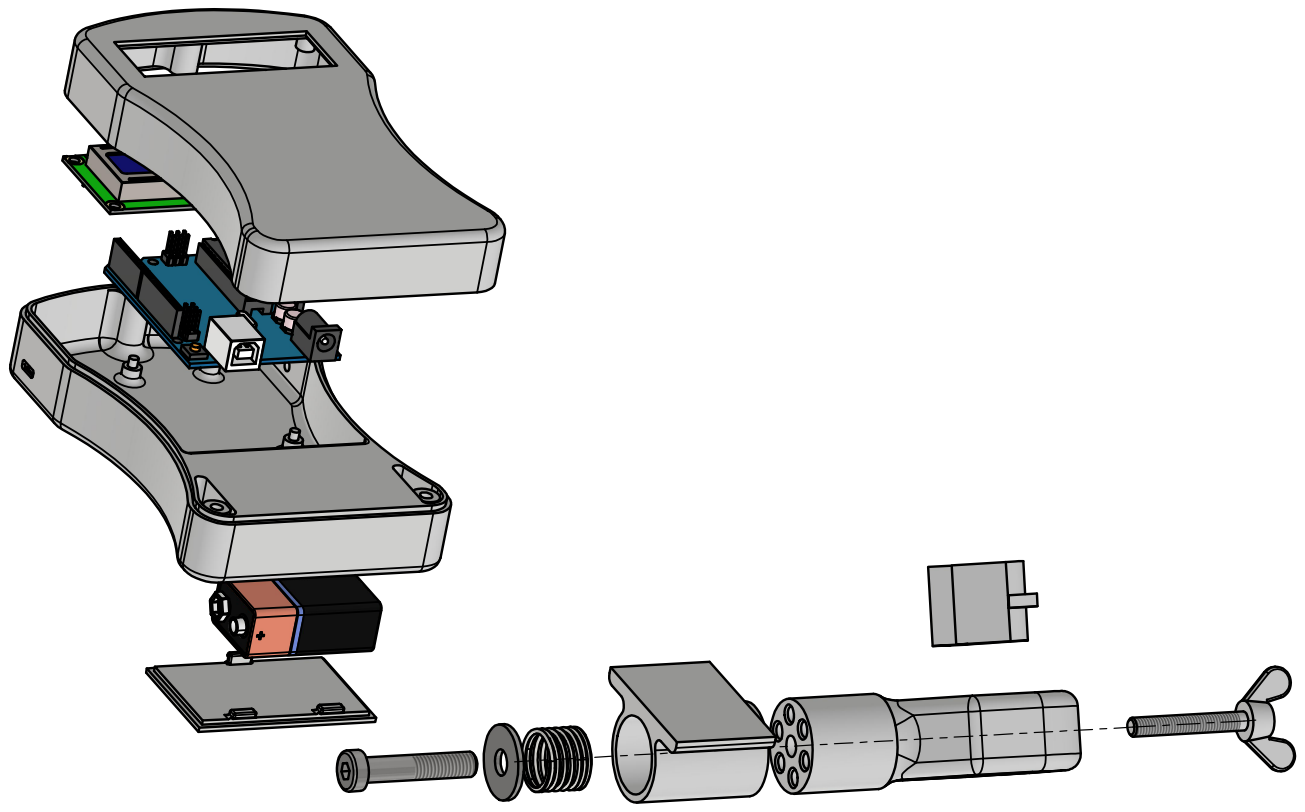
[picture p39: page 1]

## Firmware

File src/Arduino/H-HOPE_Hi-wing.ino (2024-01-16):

//Arduino 1.0.5 IDE

//include libraries for I2C and LCD display
#include <Wire.h>
#include <LiquidCrystal_I2C.h>

//LCD has i2c address 0x27 or 0x3F
LiquidCrystal_I2C lcd(0x27,16,2);

//counter
#define HALLpin 2

//variables
volatile unsigned long deltaT, deltaTold, InteruptTime=0;
float waterSpeed=0;


void setup(){
//Serial for debug
Serial.begin(19200);
//I2C begin
Wire.begin();
//LCD begin
lcd.init(); 
lcd.backlight();
lcd.setCursor(0, 0);
lcd.print("Water speed:");

//Interupt pin setup
pinMode(HALLpin, INPUT_PULLUP);
attachInterrupt(0, cnt, FALLING);
}



void loop(){ 
  
lcd.setCursor(0, 1);
//calculate water speed from frequency
waterSpeed=130.0/deltaT;  //y=130/x
//print water speed to LCD
lcd.print(waterSpeed,1);
lcd.print(" m/s");
//lcd.print(", ");
//lcd.print(deltaT);
//lcd.print(" ms   ");
//if no data from hall sensor set water speed to 0.
if(InteruptTime+1000<millis()){
  deltaT=9999;
}
//Serial print for debug
Serial.println(deltaT);
delay(200);
}


///////////////////////////////////////////////////////////////////////
//magnet detector - interrupt
void cnt() {
  deltaT=millis()-deltaTold;
  deltaTold=millis();
  InteruptTime=millis();
}
